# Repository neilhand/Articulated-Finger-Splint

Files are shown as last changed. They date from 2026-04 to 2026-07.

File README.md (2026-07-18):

# Articulated Finger Splint

> A 3D-printable articulated finger splint designed to support and protect injured fingers while preserving range of motion.

This repository contains a collection of files to support the paper "3D Printed Hinged Splint For Instability of PIP" authored by Robert White and Neil Hand.

These files are being made available to allow to allow others with better CAD capabilities (this was created by a hand therapist and an electrical enginneer with limitied CAD experience) to itterate on the design, with the ultimate aim that they can create a paratamtizable design that can be easily customized for individual patients.

These files are being made available under the CC BY 4.0 license, to allow you to freely develop and modify the design for personal or commercial use, provided you attribute the original work and authors. 

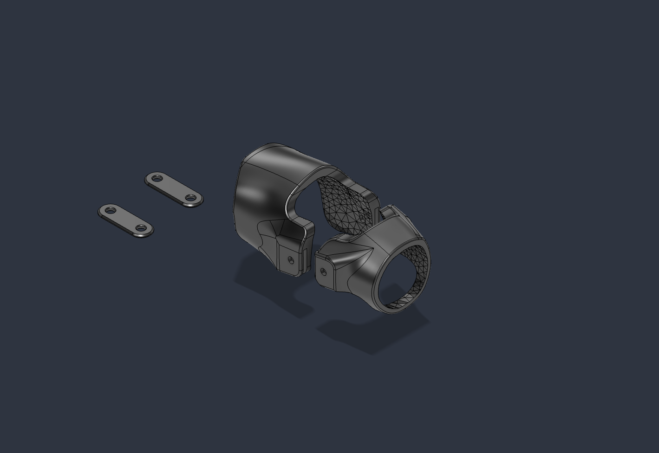
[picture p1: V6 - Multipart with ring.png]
RECOMMENDED: V6 - Multipart for FDM

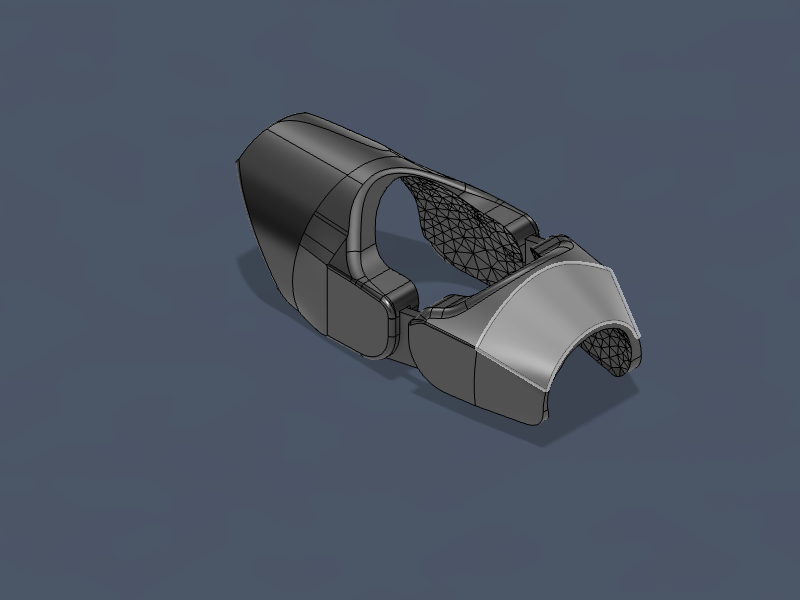
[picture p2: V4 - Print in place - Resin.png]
V4 - Print in Place for SLA/SLS


---

## Table of Contents

- [Overview](#overview)
- [Design Versions](#design-versions)
- [File Reference](#file-reference)
- [Requirements](#requirements)
- [Printing Instructions](#printing-instructions)
- [Customization](#customization)
- [Contributing](#contributing)
- [License](#license)

---

## Overview

This project provides two final splint designs optimized for FDM 3D printing:

- **V4 – Print in Place**: A single-part design with a built-in articulating hinge. No assembly required — print and wear. This version can be printed on a consumer resin printer, or preferably using a SLS or binder jet printer.
- **V5 – Multipart Print**: A two-part shell with separate connector plates. this is designed for consumer FDM printing with standard filiments. The parts are seperated to allow for printing in the orientation that provides the best strength for the parts (more info later in this doc)

Both final designs have utilised a 3D mesh scan of the injured finger to create a custom fit.

Additonal design itterations that are discussed in the paper are also included to show the evolution of the project

> ⚠️ **Medical Disclaimer**: This splint is a personal/hobbyist project and is not a certified medical device. Consult a medical professional before use for injury treatment.

---

## Design Versions

The project evolved through six iterations. Each version addressed limitations of the previous one.

| Version | Name | Description |
|---------|------|-------------|
| V0 | Multipart Box Test | Proof-of-concept for multi-part joining mechanism |
| V1 | Initial Prototype | Two-ring design with a basic external hinge |
| V2 | Fitted to Finger | Anatomically contoured inner surface based on finger mesh scan added |
| V3 | Enclosed Hinge | Hinge moved inside the body for comfoty and durability |
| V4 | Print in Place | Single-piece articulated design |
| V5 | Multipart Print | Multi-part shell with plates |
| V6 | Multipart with ring | Multi-part with front ring |

### RECOMMENDED: V6 – Multipart Print with ring to simplify usage and attachment
V6

---

## File Reference

```
Articulated-Finger-Splint/
│
├── V0 - Multipart-box-test.*       # Join mechanism prototype
├── V1 - Initial Prototype.*        # First full splint prototype
├── V2 - Fitted to Finger.*         # Anatomical fit iteration
├── V3 - Enclosed Hinge.*           # Enclosed hinge iteration
├── V4 - Print in place - Resin.*   # Single-piece print design for SLA/SLA
├── V5 - Multpart Print - FDM.*     # Multi-part print for FDM
├── V6 - Multipart with ring.*      # Simular to V5 but with a ring to simplify attachment
│
├── Buddy Strap.*                   # A 3D printed buddy strap in flexible filiment based of finger measurements   
│
├── FingerMesh.stl                  # Reference mesh of a finger for fitting
│
└── 3DModel finger/                 # Reference finger scan
    ├── OBJ/                        # OBJ format (with materials)
    └── USDZ/                       # USDZ format (AR preview on iPhone/iPad)
```

Each version includes three file types:

| Extension | Format | Use |
|-----------|--------|-----|
| `.f3d` | Fusion 360 | Full parametric source file for editing |
| `.step` | STEP / AP214 | CAD interchange (FreeCAD, SolidWorks, etc.) |
| `.png` | Image | Design preview |

---

## Design Process and Fitting

This design creates a structure that limits lateral movment using two pivot points that are positioned to allow flexion and extension while restricting side-to-side movement. These pivots do not need to handle much direct force since when one is in compression the other is in extension, spreading the forces. As such, they can be relatively simple and lightweight.

The most important part of the design was identifying the correct placement of the dual pivot points on the splint to ensure proper articulation and comfort. This was achived through multiple iterations and prototypes across multiple versions of the design.

It bagan with marking the injured fingers with a sharpie at the desired location, an image of the finger including the placement was then important into CAD and used as the initial reference for the pivots. Subsequent iterations were then made to adjust the placement of the pivots to ensure proper articulation. You will find some of these images in the f3d files as canvases.

Early versions of the design used a rough appoximation of the injured finger based on the previously mentioned images. This was effective, but resulting in sharper edges and presure points. This was initially addressed by adding a soft layer of material to the splint, but this was fiddly and not ideal for long term use. The final design addresses this by using a detailed scan of the finger and subtracting that mesh from the final design for a perfect fit.

For this project the mesh was created by creating a plaster cast of the finger and then scanning it using an iPhone app meant for photogrammetry (generating a 3D model from multiple images or video). This was chosen rather than a direct finger scan as keeping the finger still for an extended period of time was not possible. This could be address using a structured light scanner or other similar technology, which could scan more accurately and quickly. If the spint is only needed for a short period of time, the approximation could be used.

## Requirements

### Software
- [Autodesk Fusion 360](https://www.autodesk.com/products/fusion-360) (to edit `.f3d` source files)
- Any CAD tool supporting STEP files (FreeCAD, SolidWorks, Onshape, etc.) for `.step` files
- A slicer such as [Bambu Studio](https://bambulab.com/en/download/studio), [PrusaSlicer](https://www.prusa3d.com/page/prusaslicer_424/), or [Ultimaker Cura](https://ultimaker.com/software/ultimaker-cura/)

### Hardware
- **V4**: Resin, SLS, binderjet printing or similer technology. This can be done at home or through a service provider such as PCBWay in the case of the Nylon version that has been used extensively.
- **V6**: FDM printer with a preffered nozzle diameter of 0.4mm. 

#### Materials
| Material | Notes |
|----------|-------|
| **PLA** | Rigid; easy to print but brittle |
| **PETG** | Good balance of printability and durability |

---

## Printing Instructions

### V4 – Print in Place (Single Part)

> This was pinted on both a consumer grade resign printer as well as a industrial  binderjet printer (PCBway. Another vendor was also used, but the quality was sub par and the parts were either two fragile or did not articulate).

The part is orientated such that the hinge is printed in the open/extended position and parallel to the print plane regardless of printing process. This mazimizes the chance of successful printing and articulation.

The choice of resin seems to be very important and the more opaque the resin the higher the chance of success. The print must be removed from support material and cleaned thoroughly to ensure proper articulation prior to UV curing.

>**A note on failure modes and chice of resin or printing technology**  
The resin used for the prototyping was a standard gray 8K photopolymer resin. This resulted in a good part and high success rate, but there wer concerns about the sudden snap of the parts under stress. The Nylon printed parts have shown to be more durable and less prone to sudden failure as the deform rather than snap.

### V6 – Multipart Print
> This was designed to be printed on a consumer grade FDM printer.
The hing parts are printed flat to ensure maximum strength and minimize warping. Minimal supports were used (painted on) and orientation is shown in the image below. 

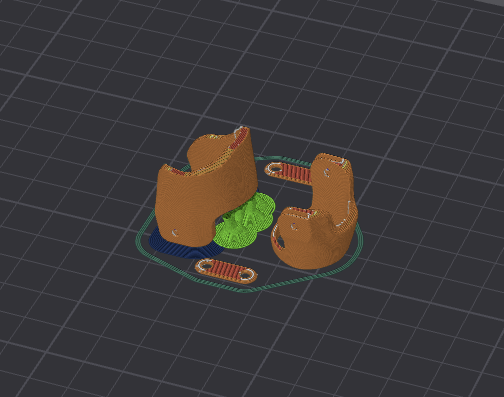
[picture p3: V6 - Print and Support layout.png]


The hinges are held in place using a small piece of 1.75mm PLA filament that is inserted into the hinge and then the end melted smooth with the surface using a soldering iron or similar tool.

This multipart design was created to allow for easier printing and assembly especially in a clinical environment. The parts are small and can be printed quickly, it is also possible a mixed collection of part can be mixed and matched to create a close enough fit for many without neededing special design and finger scanning

Things to note on the V6 version. The hinges are slightly different sizes to have the shorter on the left hand side to provide preloading of the 

---

## Customization

There is no customization available at this time and the `.f3d` source files are provided to show how the parts were designed and allow for modification and evolution hopefully towards a fully parametic design. Unfortunaly due to poor file management some of the history and timeline data is not available.

---

## Contributing

Contributions, improvements, and remixes are welcome!

1. Fork this repository.
2. Create a feature branch: `git checkout -b feature/my-improvement`
3. Commit your changes: `git commit -m 'Add my improvement'`
4. Push to the branch: `git push origin feature/my-improvement`
5. Open a Pull Request.

---

## License

This project is licensed under the [Creative Commons Attribution 4.0 International (CC BY 4.0)](https://creativecommons.org/licenses/by/4.0/) license — you are free to share and adapt the design for any purpose, provided appropriate credit is given.

---

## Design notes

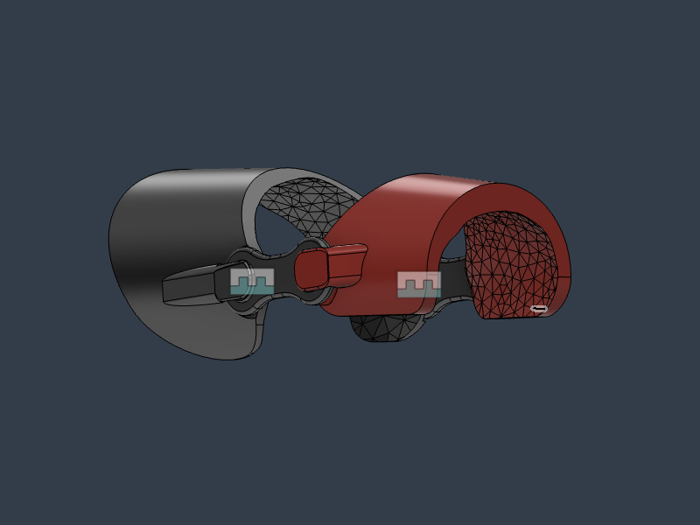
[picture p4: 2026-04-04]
V2 - Fitted to Finger.png

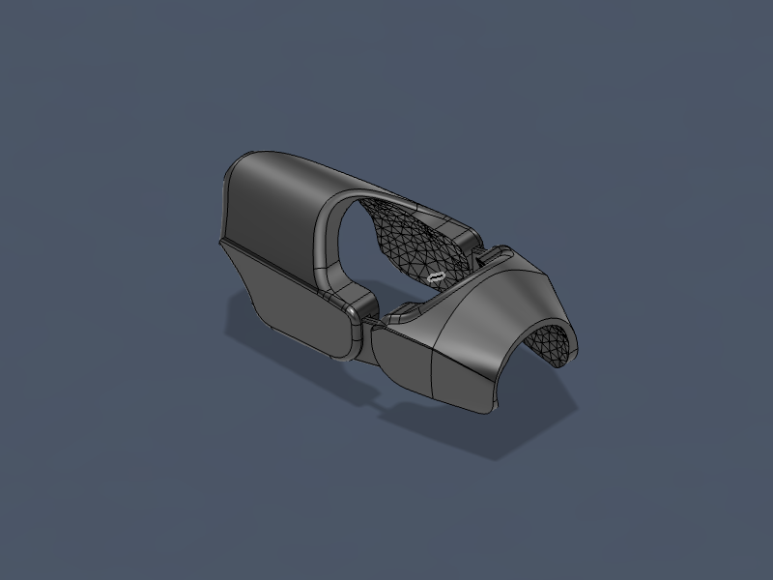
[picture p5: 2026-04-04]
V3 - Enclosed Hinge.png

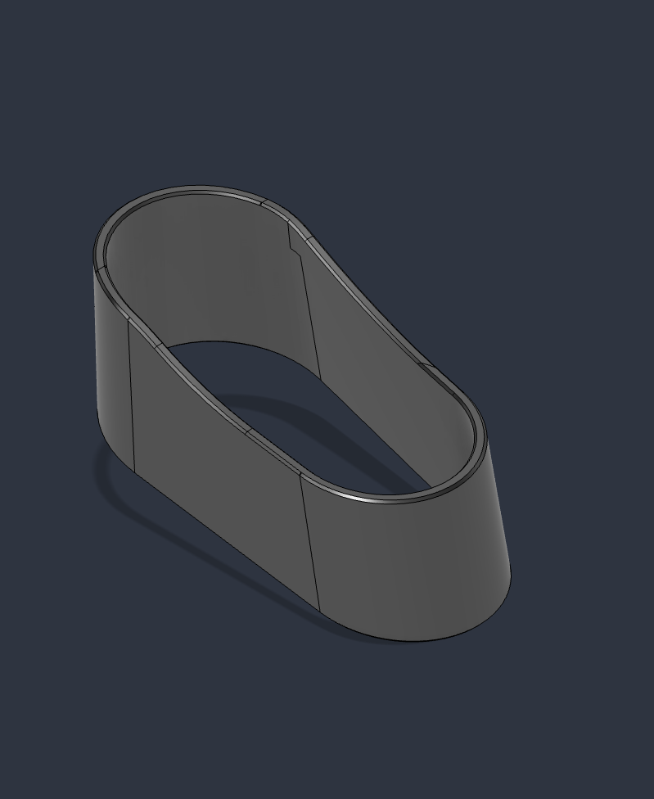
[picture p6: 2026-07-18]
Buddy Strap.png

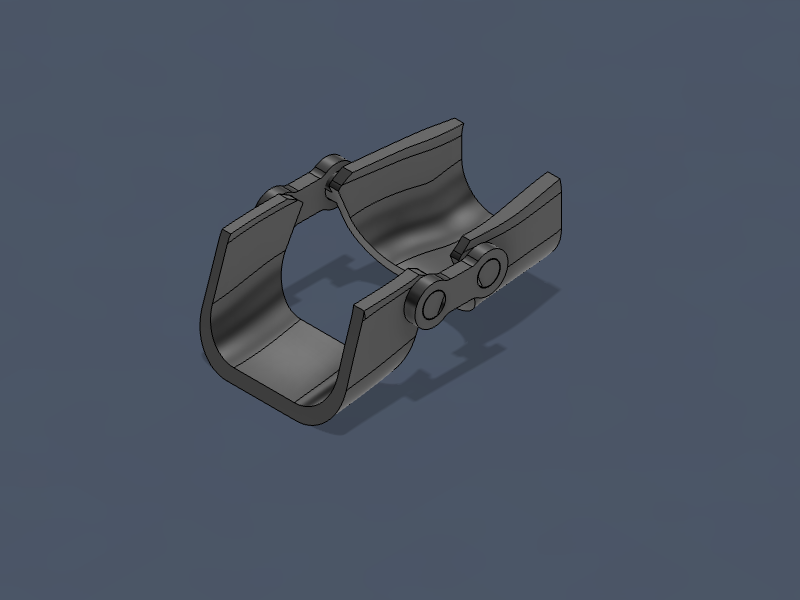
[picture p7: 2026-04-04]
V1 - Initial Prototype.png

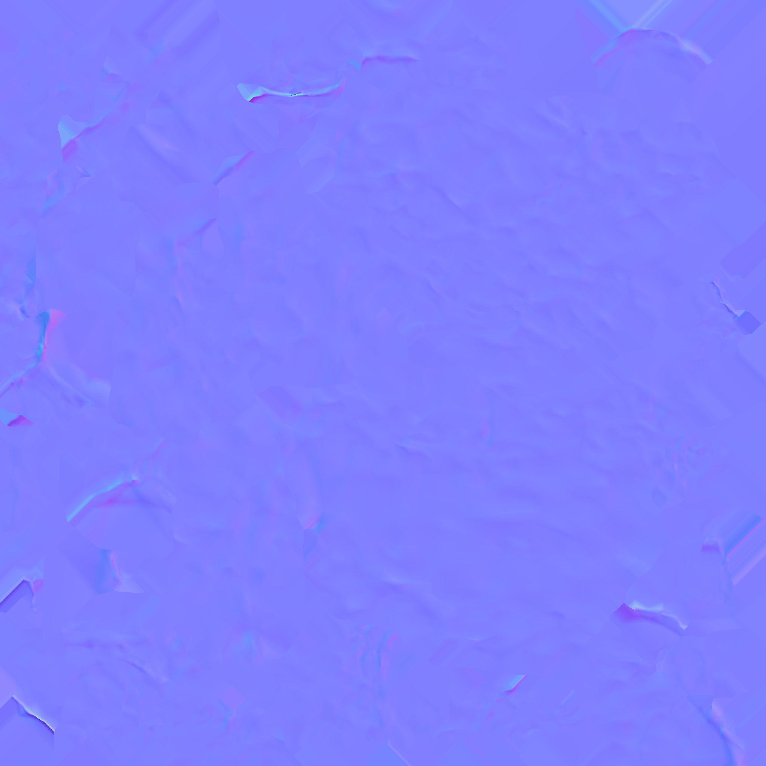
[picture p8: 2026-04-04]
3DModel finger/OBJ/3DModel/baked_mesh_norm0.png

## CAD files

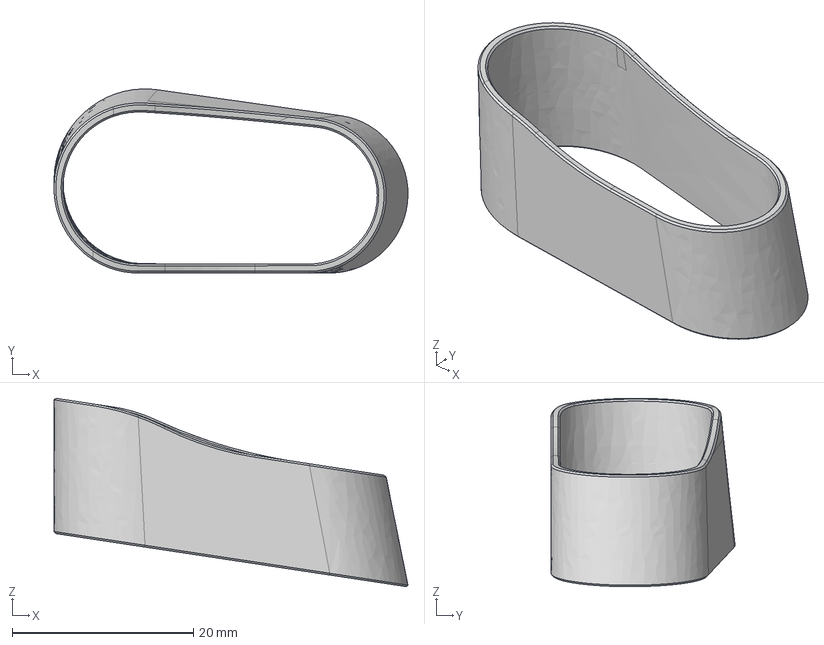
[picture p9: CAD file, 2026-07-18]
Buddy Strap.step
39.1 x 20.3 x 20.8 mm

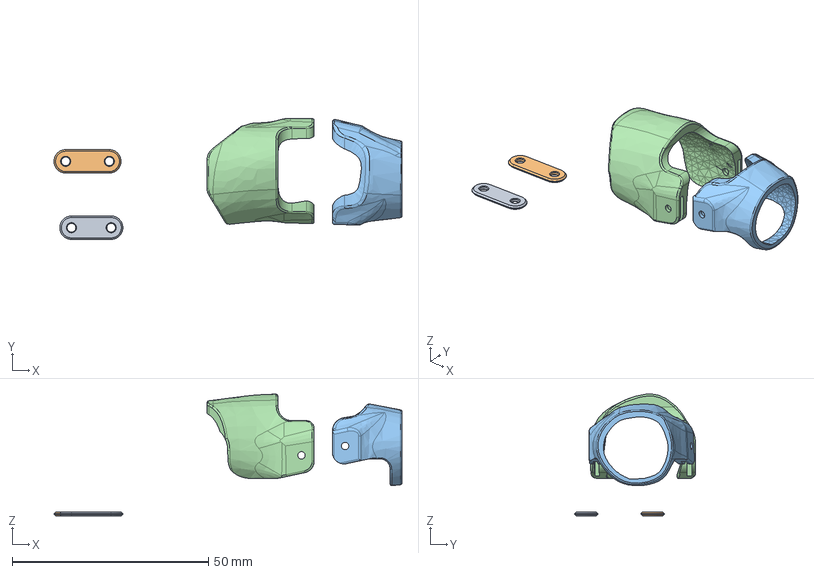
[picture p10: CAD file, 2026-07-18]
V6 - Multipart with ring.step
88.7 x 30.8 x 31.1 mm
Hinge - left
hinge - right
front
back

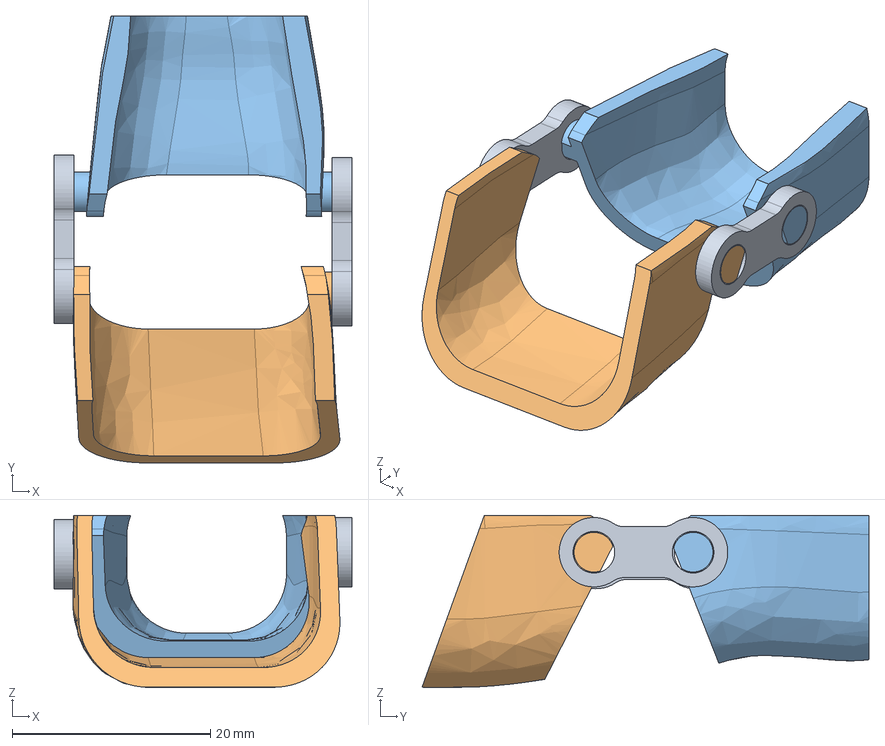
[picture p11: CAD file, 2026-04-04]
V1 - Initial Prototype.step
30.0 x 45.1 x 17.4 mm
hinge x 2
top back
top front

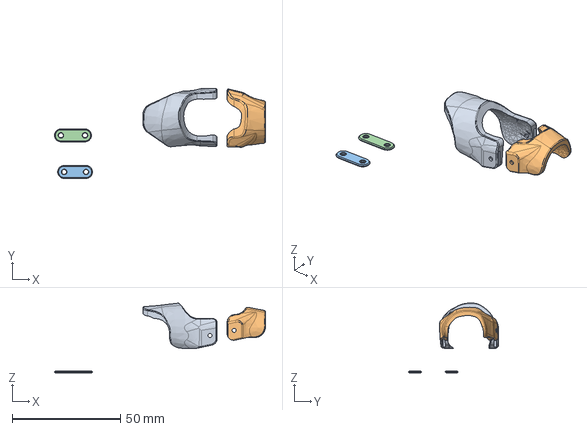
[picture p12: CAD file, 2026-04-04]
V5 - Multpart Print - FDM.step
97.5 x 41.6 x 32.3 mm

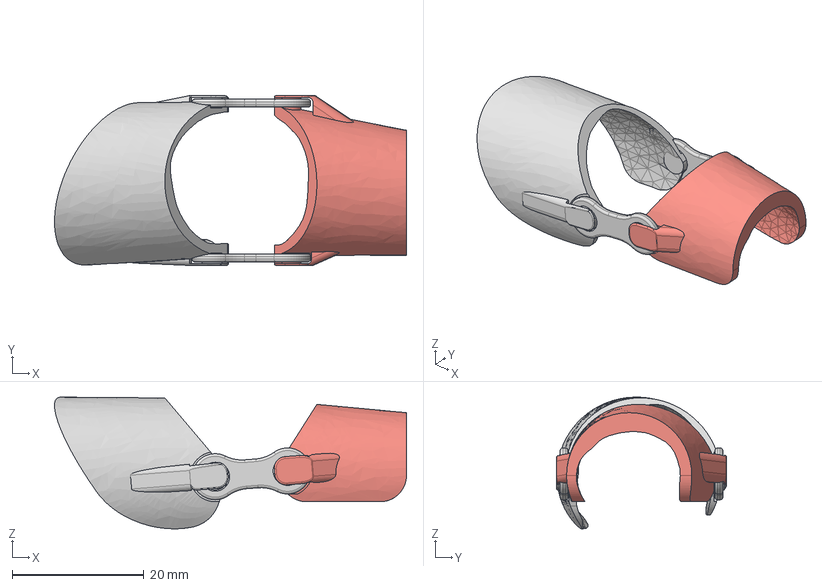
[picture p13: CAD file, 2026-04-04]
V2 - Fitted to Finger.step
53.4 x 25.8 x 20.0 mm
Rear
front
Hinge x 2

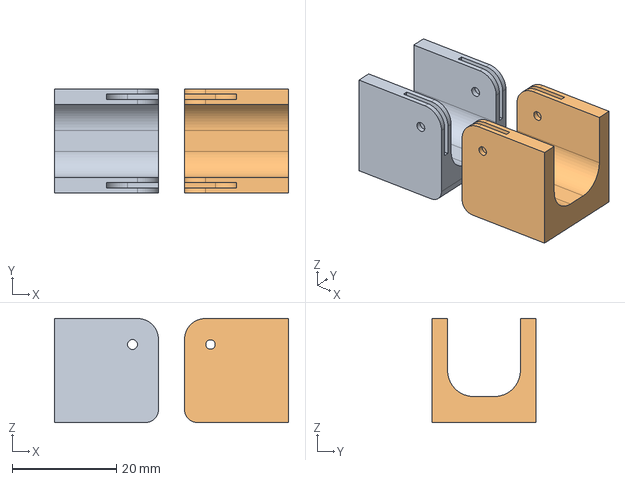
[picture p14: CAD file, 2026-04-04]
V0 - Multipart-box-test.step
45.0 x 20.0 x 20.0 mm

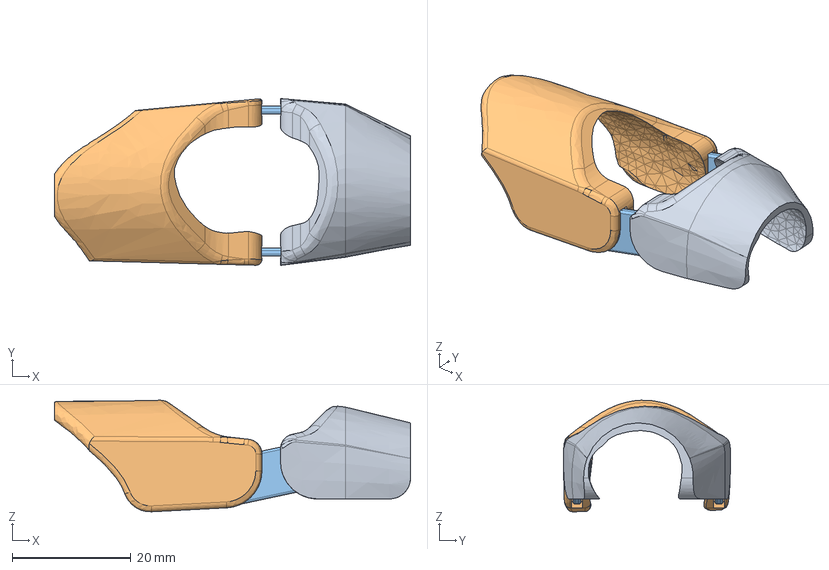
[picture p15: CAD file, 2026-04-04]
V3 - Enclosed Hinge.step
59.9 x 28.1 x 18.8 mm
front Splint (1)
back splint
hinge x 2

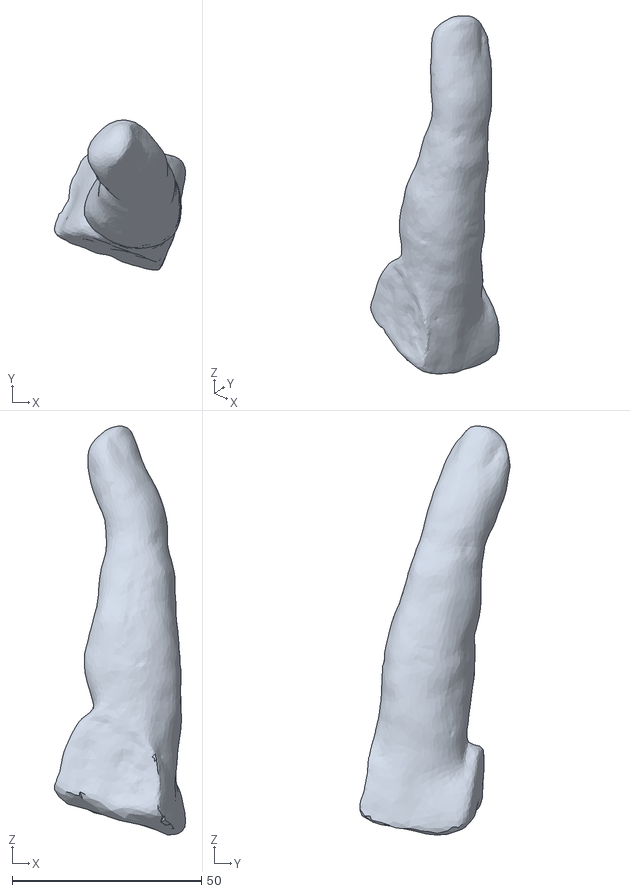
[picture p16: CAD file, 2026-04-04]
FingerMesh.stl
34.7 x 39.7 x 108.0

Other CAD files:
V4 - Print in place - Resin.step
Buddy Strap.f3d
V0 - Multipart-box-test.f3d
V4 - Print in place - Resin.f3d
V5 - Multpart Print - FDM.f3d
V6 - Multipart with ring.f3d

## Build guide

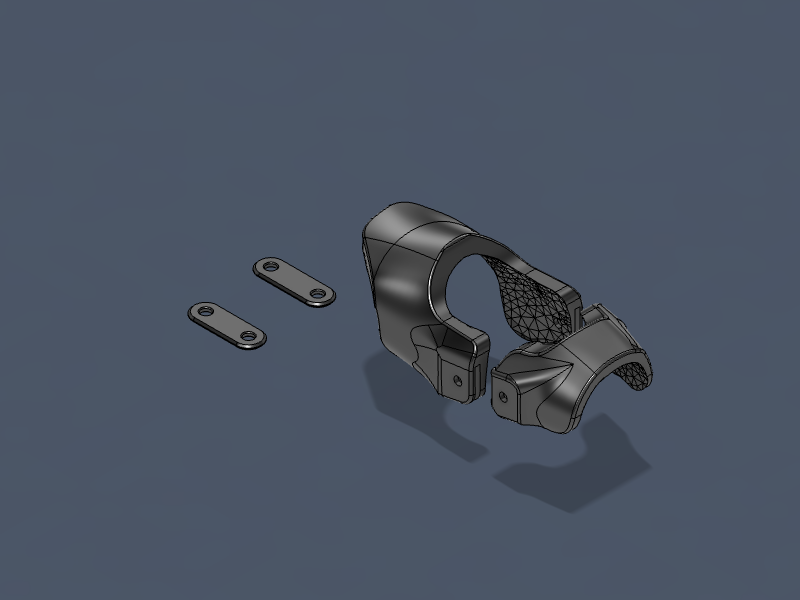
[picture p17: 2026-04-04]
V5 - Multpart Print - FDM.png
